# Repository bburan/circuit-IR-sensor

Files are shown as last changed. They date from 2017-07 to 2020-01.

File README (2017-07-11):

Overview
--------

This is a circuit that provides power for up to 4 infrared
emitter/phototransistor pairs. The photodiode current is converted to voltage
and low-pass filtered cutoff frequency approx. 150 Hz). Holes are designed for
a 4-40 screw (a common size in standoffs). The circuit is designed to work with
the OPS693 phototransistor LED/sensor matched pair. The 3D models of the food
hopper and nose-pokes are designed with the dimensions of the OPS693 in mind.
This requires a 5VDC power supply.

Assembly
--------

Design files generated using KiCAD. The Gerber files can be uploaded to a PCB
manufacturer such as Macrofab. Total cost for a fully assembled circuit from
Macrofab is roughly $15. Once the assembled board arrives, you'll need to
either solder wires directly to the holes or use 0.1" (2.54mm) pitch header
pins. The Pheonix MPT screw terminal blocks also work very well as they have
the same pin spacing.

License
-------

This project is licensed under the Creative Commons Attribution 4.0
International license.

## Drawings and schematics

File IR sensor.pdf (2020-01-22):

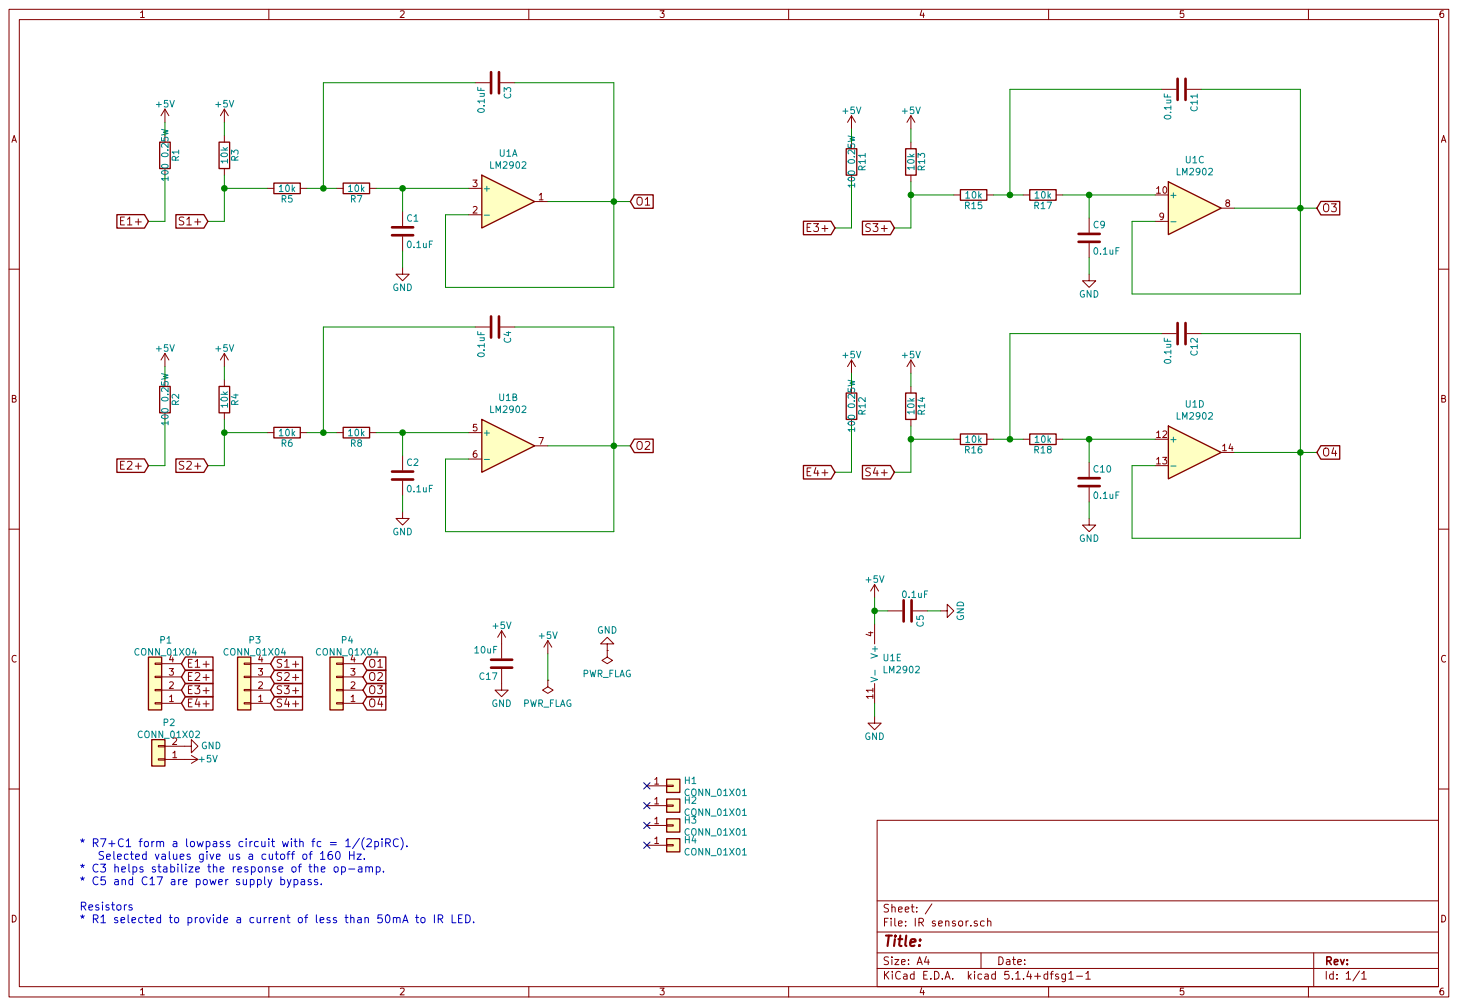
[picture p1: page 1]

* R7+C1 form a lowpass circuit with fc = 1/(2piRC).
Selected values give us a cutoff of 160 Hz.
* C3 helps stabilize the response of the op-amp.
* C5 and C17 are power supply bypass. Resistors

Id: 1/1 Title: File: IR sensor.sch Sheet: /

* R1 selected to provide a current of less than 50mA to IR LED.

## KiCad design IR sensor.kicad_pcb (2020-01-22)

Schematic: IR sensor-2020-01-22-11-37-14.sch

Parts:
C1, C2, C3, C4, C5, C9, C10, C11, C12: 0.1uF; C_0603
C17: 10uF; C_1206
H1, H2, H3, H4: CONN_01X01; 1pin
P1, P3, P4: CONN_01X04; Pin_Header_Straight_1x04
P2: CONN_01X02; Pin_Header_Straight_1x02
R1, R2, R11, R12: 100 0.25W; R_1206
R3, R4, R5, R6, R7, R8, R13, R14, R15, R16, R17, R18: 10k; R_0402
U1: TLV2774; TSSOP-14_4.4x5mm_Pitch0.65mm

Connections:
E1+: P1.4, R1.2
E2+: P1.3, R2.2
E3+: P1.2, R11.2
E4+: P1.1, R12.2
GND: C1.2, C2.2, C5.1, C9.2, C10.2, C17.1, P2.2, U1.11 (V-)
unnamed: C1.1, R7.1, U1.3 (+)
unnamed: C2.1, R8.1, U1.5 (+)
unnamed: C3.2, R5.1, R7.2
unnamed: C4.2, R6.1, R8.2
unnamed: C9.1, R17.1, U1.10 (+)
unnamed: C10.1, R18.1, U1.12 (+)
unnamed: C11.2, R15.1, R17.2
unnamed: C12.2, R16.1, R18.2
O1: C3.1, P4.4, U1.1, U1.2 (-)
O2: C4.1, P4.3, U1.6 (-), U1.7
O3: C11.1, P4.2, U1.8, U1.9 (-)
O4: C12.1, P4.1, U1.13 (-), U1.14
S1+: P3.4, R3.2, R5.2
S2+: P3.3, R4.2, R6.2
S3+: P3.2, R13.2, R15.2
S4+: P3.1, R14.2, R16.2

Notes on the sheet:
* R7+C1 form a lowpass circuit with fc = 1/(2piRC). Selected values give us a cutoff of 160 Hz. * C3 helps stabilize the response of the op-amp. * C5 and C17 are power supply bypass. Resistors * R1 selected to provide a current of less than 50mA to IR LED.

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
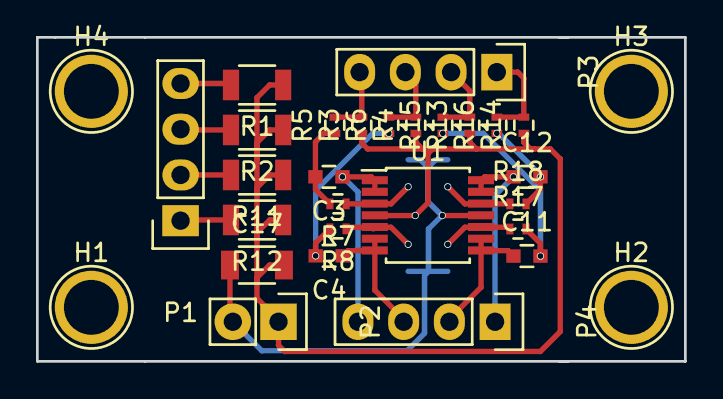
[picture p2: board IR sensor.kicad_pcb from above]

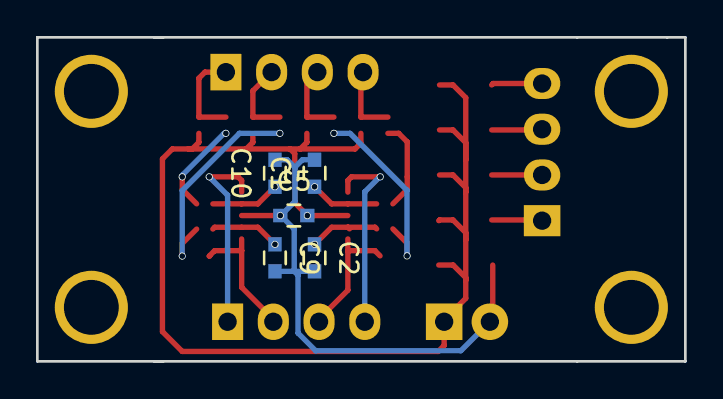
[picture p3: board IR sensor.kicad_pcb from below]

Board: 2 copper layers, 36.0 x 18.0 mm, 35 parts (5 on the bottom side), 22 nets.

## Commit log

2015-12-18 ENH: Added IR sensor circuit
    [IR sensor.kicad_pcb, IR sensor.sch]
2016-02-17 ENH: Updates to IR sensors
    [IR sensor.kicad_pcb, IR sensor.sch]
2017-07-11 ENH: Make PCB more compact
    [IR sensor.kicad_pcb, IR sensor.sch]
2017-07-11 Add gerber outputs
    [IR sensor-B.Cu.gbl, IR sensor-B.Mask.gbs, IR sensor-B.Paste.gbp, IR sensor-B.SilkS.gbo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]
2017-07-11 Add readme and bill of materials
2020-01-22 Commit before modifications
    [IR sensor.dsn]
2020-01-22 Update to KiCAD 5
    [IR sensor-2020-01-22-11-37-14.sch, IR sensor.kicad_pcb]
